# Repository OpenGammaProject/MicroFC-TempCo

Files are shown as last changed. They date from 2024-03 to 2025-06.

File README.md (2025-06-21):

# MicroFC SiPM Temperature Compensation

PCB to temperature compensate the gain of a C-Series MicroFC silicon photomultiplier by [onsemi](https://www.onsemi.com/pdf/datasheet/microc-series-d.pdf). Diesnged as a passthrough for the SiPM bias voltage. You can buy all the parts and the PCB using [Kitspace](https://kitspace.org/opengammaproject/MicroFC-TempCo) (non-affiliated).

PCB size is 20 x 40 mm, which is a lot larger than it needs to be, but it's nicer to use with cables this way and solder everything in place.

<p align="center">
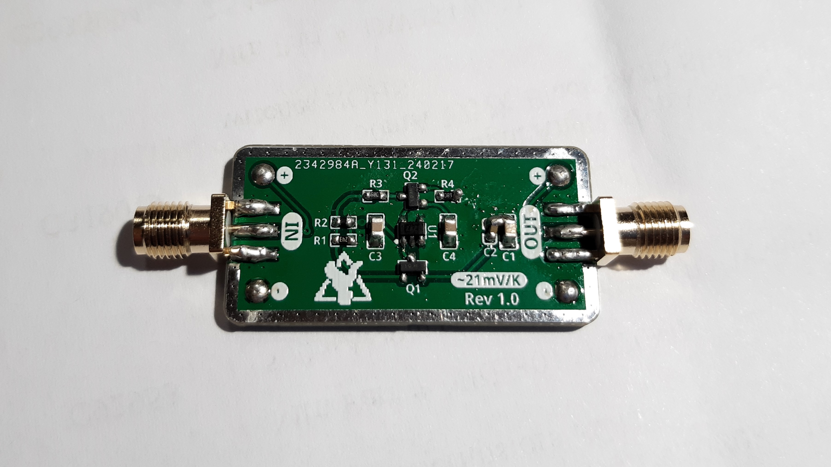
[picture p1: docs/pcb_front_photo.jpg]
Front Side PCB
  
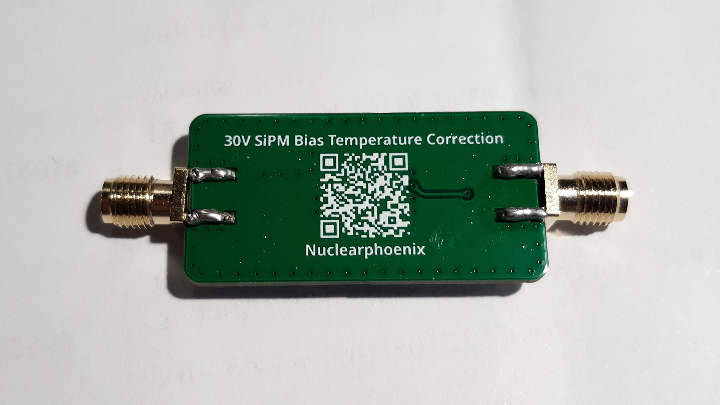
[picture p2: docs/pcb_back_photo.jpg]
Back Side PCB
  
</p>

<p align="center">
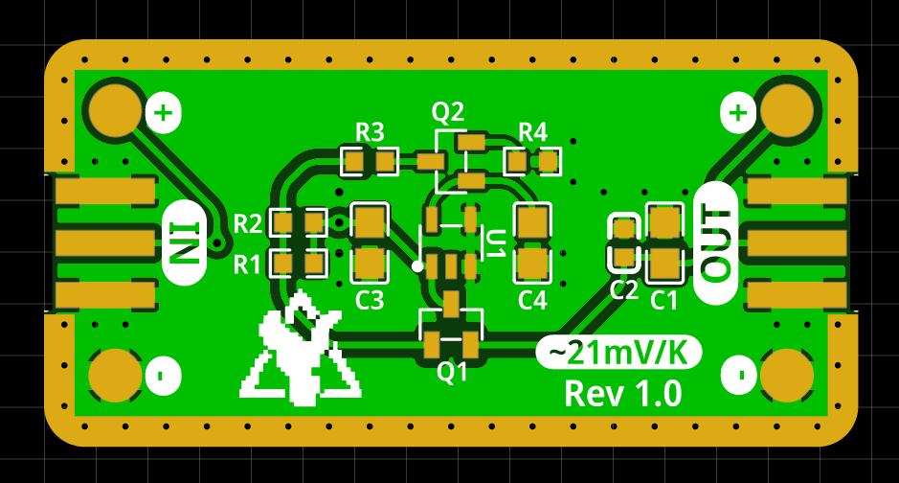
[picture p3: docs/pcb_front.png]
Front Side PCB Rendering
  
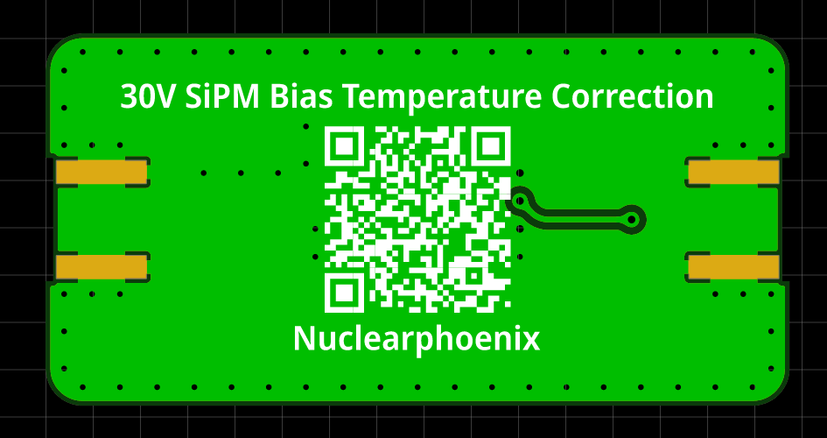
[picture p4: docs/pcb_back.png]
Back Side PCB Rendering
  
</p>

The temperature compensation circuitry is based on a [paper by Evgeny Kuznetsov](https://doi.org/10.1016/j.nima.2017.11.060) (Temperature-compensated silicon photomultiplier) and aims to roughly support the 21 mv/K slope of the SiPM. Research and testing was at first mostly done by [@sebyon](https://github.com/sebyon), thanks a lot!

However, upon re-testing on a heated 3D printer bed in ranges of 20°C - 50°C it looks more like ~14 mV/K. This might very well be caused by the testing setup. The print bed does not deliver exact temperature values and my multimeter might be off a little bit too. The possibility that different loads affect the slope of the compensation must also be researched in the future. In this testing, there was not load attached except for the multimeter. The whole setup was allowed a 20 minute stablizing period before measuring between each temperature step.

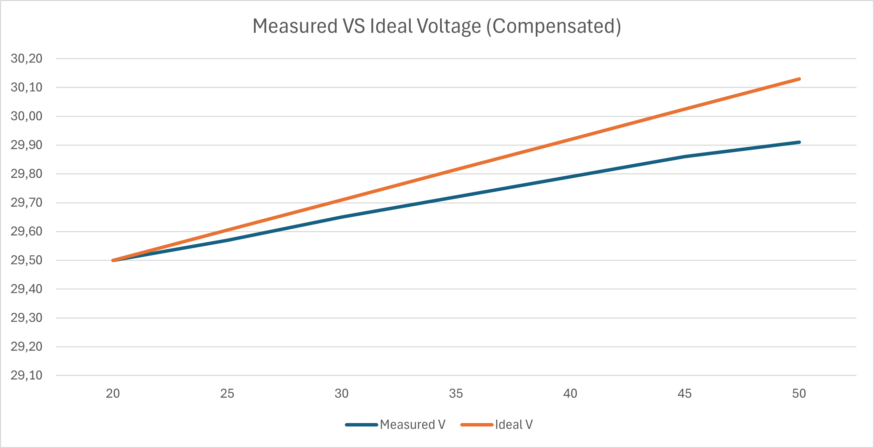
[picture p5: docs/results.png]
Results Plot


The board features standard SMA edge connectors, which can be used with standard SMA cables to connect between the power supply and the SiPM. Alternatively, you can also solder your own wires to the corresponding pads.



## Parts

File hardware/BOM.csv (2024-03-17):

ID | Name | Designator | Footprint | Quantity | Manufacturer Part | Manufacturer | Supplier | Supplier Part | Price
1 | 4.7uF | C1,C3,C4 | C0805 | 3 | CL21A475KBQNNNE | SAMSUNG(三星) | LCSC | C98192 | 0.024
2 | 100nF | C2 | C0603 | 1 | CL10B104KC8NNNC | SAMSUNG(三星) | LCSC | C15725 | 0.008
3 | MMBT5088LT1G | Q1,Q2 | SOT-23-3_L2.9-W1.3-P1.90-LS2.4-BR | 2 | MMBT5088LT1G | onsemi(安森美) | LCSC | C232555 | 0.057
4 | 24kΩ | R1 | R0603 | 1 | AR03BTCX2402 | Viking(光颉) | LCSC | C319717 | 0.034
5 | 10KΩ | R2 | R0603 | 1 | NTCS0603E3103FLT | VISHAY(威世) | LCSC | C142556 | 0.393
6 | 49.9kΩ | R3,R4 | R0603 | 2 | RT0603BRD0749K9L | YAGEO(国巨) | LCSC | C705780 | 0.025
7 | TPS7B6950DBVR | U1 | SOT-23-5_L3.0-W1.7-P0.95-LS2.8-BL | 1 | TPS7B6950DBVR | TI(德州仪器) | LCSC | C174327 | 0.376
8 | BWSMA-KE-P001 | U2,U3 | SMA-SMD_BWSMA-KE-P001 | 2 | BWSMA-KE-P001 | BAT WIRELESS | LCSC | C496550 | 0.355

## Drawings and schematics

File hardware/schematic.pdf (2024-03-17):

## Temperature Correction: ~21 mV/K

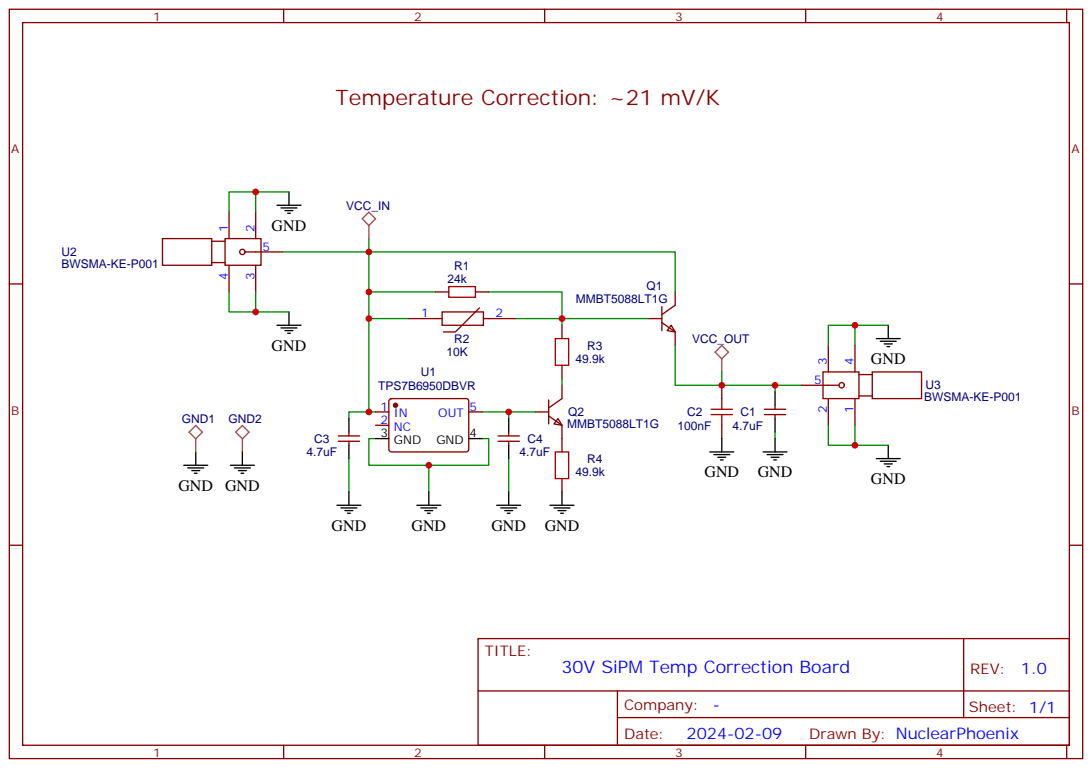
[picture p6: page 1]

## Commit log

2024-03-18 [ImgBot] Optimize images
    *Total -- 1,636.91kb -> 1,474.57kb (9.92%)
    /docs/pcb_back.png -- 47.88kb -> 24.27kb (49.32%)
    /docs/pcb_front.png -- 81.67kb -> 45.60kb (44.17%)
    /docs/pcb_back_photo.jpg -- 588.01kb -> 543.55kb (7.56%)
    /docs/pcb_front_photo.jpg -- 836.79kb -> 781.64kb (6.59%)
    /docs/results.png -- 82.56kb -> 79.52kb (3.68%)
2025-02-22 add pick and place file
    [PickAndPlace_PCB.csv]
